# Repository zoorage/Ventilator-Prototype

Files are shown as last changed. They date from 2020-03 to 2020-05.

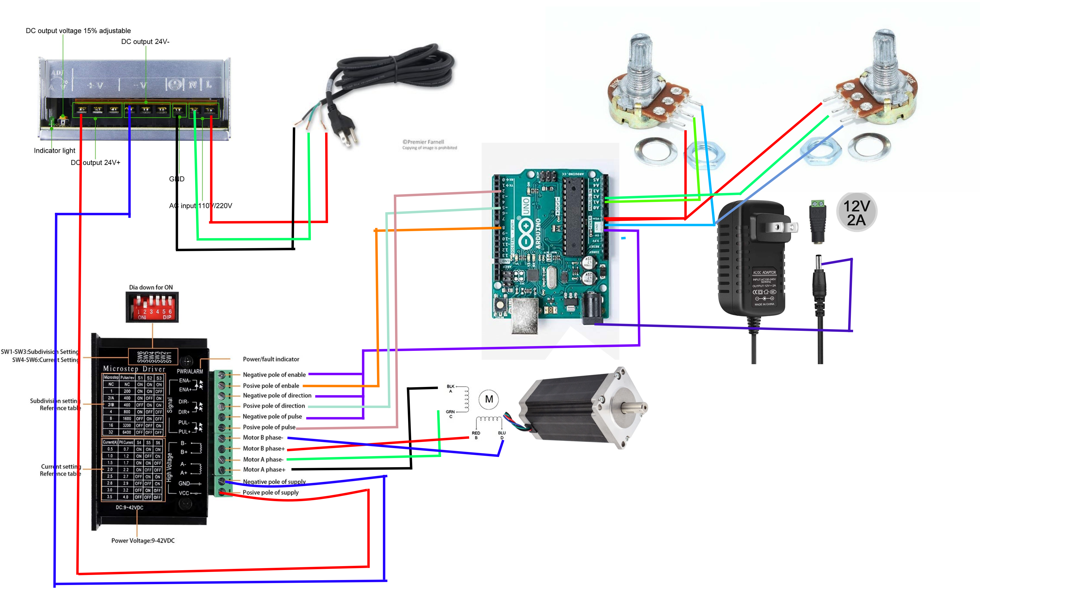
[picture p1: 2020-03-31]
Wiring Diagram.png

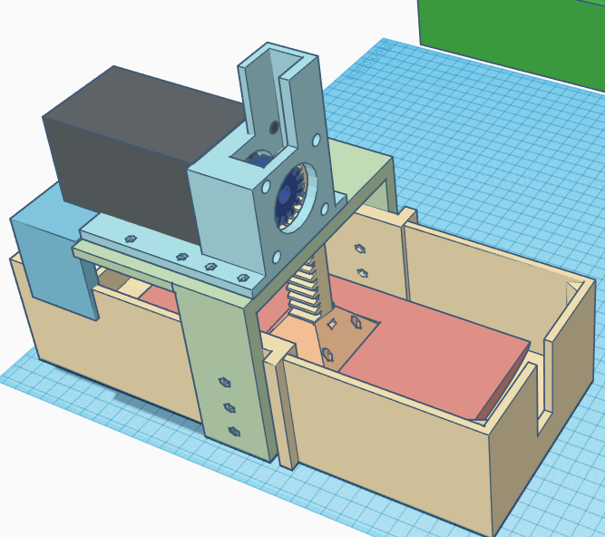
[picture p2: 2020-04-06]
3D Print Files/Vent Side 2.PNG

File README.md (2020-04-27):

# Ventilator-Prototype: Bridge to Mechanical Ventilation (Bridge)

Heads up, I have not been able to update the wiring diagram. The instructions has all the connections in it though.
Also, I will update the arduino sketch once I had the time to do a little more testing with the LED and reset/test button.

If anyone has experience with FDA applications for EUA and are able to help with this process, please contact me. I can use all the help I can get.

Disclaimers
1. This device is not approved by FDA or any other regulatory body.
2. This is not a ventilator or replacement for ventilators.
3. This device should never be used on a patient while there is an FDA approved device available.
4. Only practitioners who are fully competent in managing critically ill patients should consider this device.
5. There is absolutely no clinical testing done on this device. This device should be considered very high risk, and extreme caution should be exercised to consider using this device on a human being. In other workd, the only time the benefit of using this device may outweigh the risks would be when the patient is faced with certain death due to absence of any FDA approved devices or therapies.
6. Our team has provided this instruction as good samaritans for everyone and will not accept liability for any damages that the use of this device may cause.
7. Anyone who follows this instruction agrees to follow all the loal and federal regulatory protocols for compassionate use of investigational new devices and if applicable inform all the regulatory bodies such as FDA or local IRB.

This is an effort to create a make shift device to bridge patients infected with COVID-19 who need mechanical ventilation only when there is no ventilator available

I am an anesthesiologist with no real technical background.
Basically, this is a simple prototype that is easily reproducible and costs about $100. It can be made very quickly and does not require any technical expertise.
I started working on this last week, when I heard about the total number of ventilators in my state and the number that we think we're going to need. In the back of my mind, I kept telling myself that we can just use a bag and ventilate the patients with hand, but we are going to have a drastic shortage of man power too. So I decided to make a system that would replace hand ventilation and is cheap, easy and NEVER TO BE USED ON A PATIENT unless shortage of ventilators mean my patient with a reversible respiratory failure is going to die. That is the only time that I would use a system like this. 
Once I fix my 3D printer's bed, I will post the more elegant prototype. 
Here I'm using and arduino with DRV 8825 driver for a NEMA 17 stepper motor. 
I'm working on a few other prototypes too and once I can do more testing, I will post the STL files, arduino sketch and the part list.
Again, this is not a ventilator replacement; this is only to be used when patients have no other options and will simply die without a ventilator.

My team is working on the FDA's EUA application and I will provide updates as soon as I can.

Shield: [][cc-by]

This work is licensed under a [Creative Commons Attribution 4.0 International
License][cc-by].

[][cc-by]

[cc-by]: http://creativecommons.org/licenses/by/4.0/
[cc-by-image]: https://i.creativecommons.org/l/by/4.0/88x31.png
[cc-by-shield]: https://img.shields.io/badge/License-CC%20BY%204.0-lightgrey.svg

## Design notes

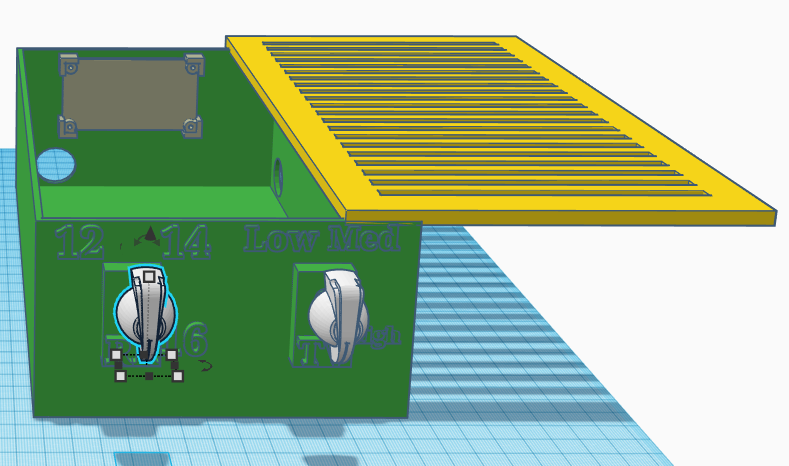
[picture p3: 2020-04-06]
3D Print Files/Vent-Electronics Box.PNG

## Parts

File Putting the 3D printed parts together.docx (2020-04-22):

Assembly of 3D-Printed Parts

1. Insert an M3 not in the circled slot on the gear and fasten an M3 bolt gently into it so that it won’t move.

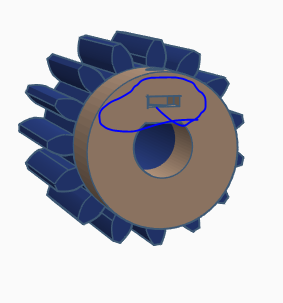
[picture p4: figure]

2. Insert the gear over the shaft of the motor. This has to be a tight fit. You may need to use a heat gun, blow drier, or a press.

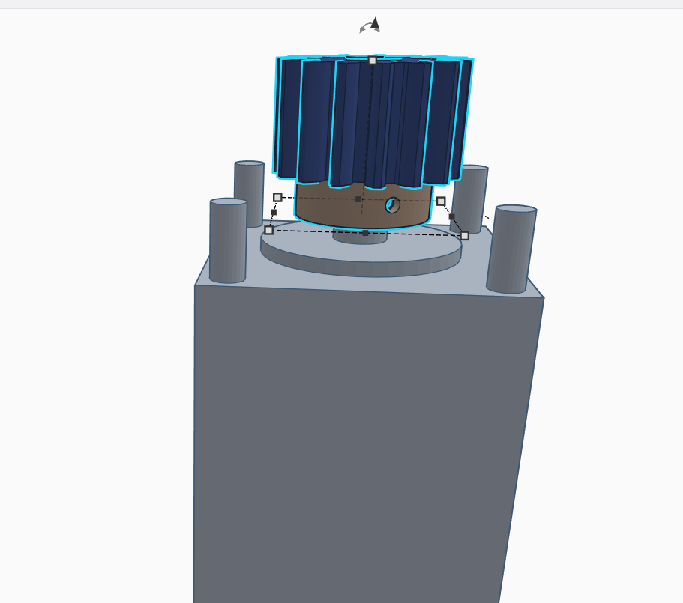
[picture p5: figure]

3. Use m4 nuts and bolts for the stepper motor and the motor cage.

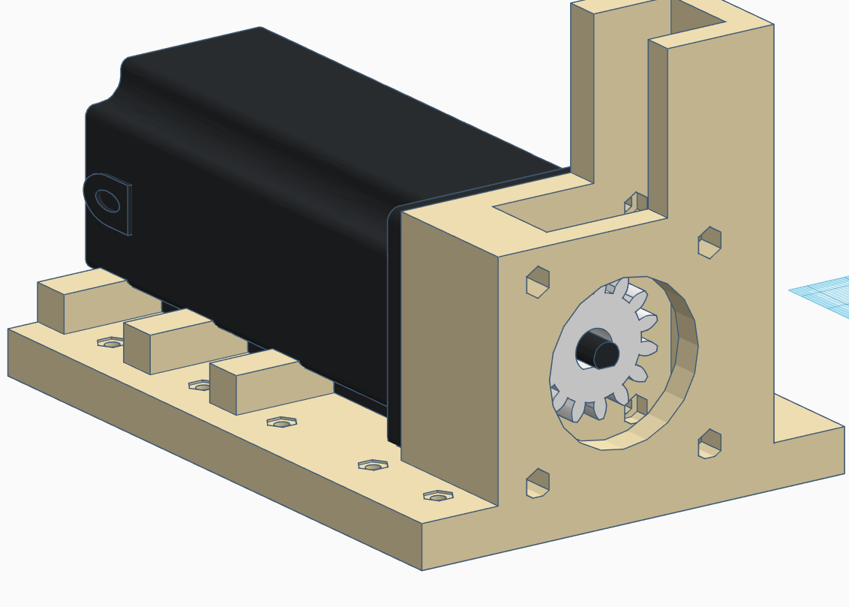
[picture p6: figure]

4. Use m2 nuts and bolts to secure the motor cage to the bridge.

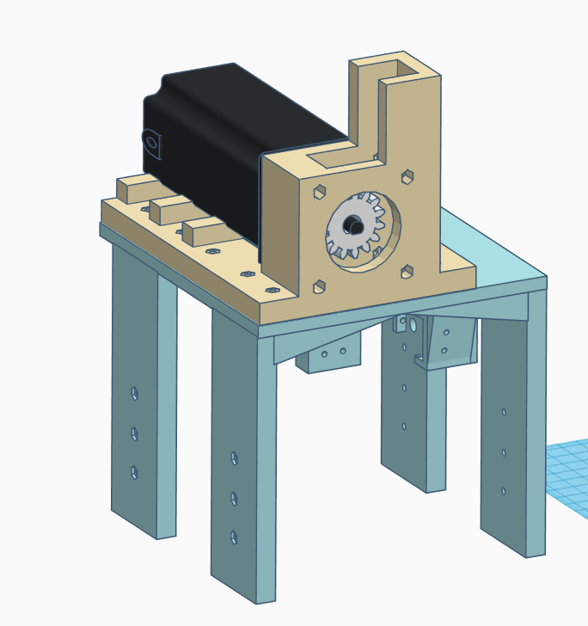
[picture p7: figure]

5. Insert an M3 nut in to the rack

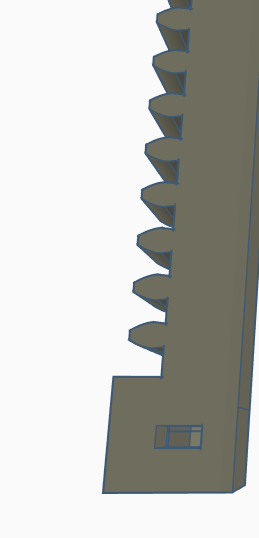
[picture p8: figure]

6. Place the rack into the rack base and insert an m3 bolt into the slot.

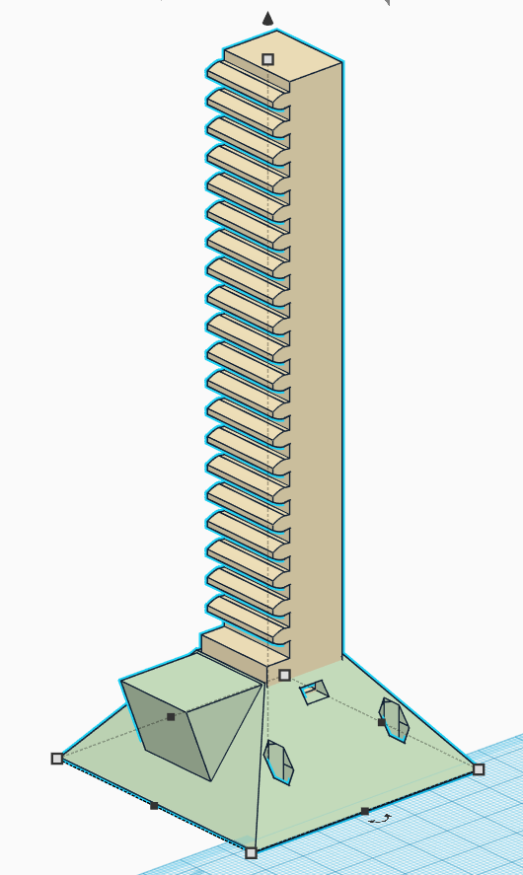
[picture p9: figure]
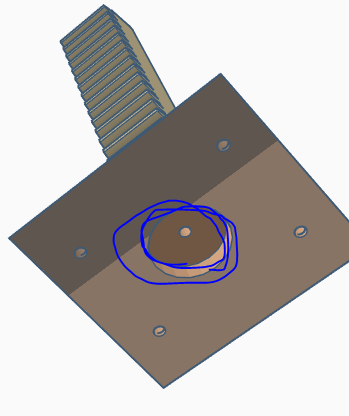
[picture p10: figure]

7. Use M3 nuts and bolts to secure the rack base to the plate.

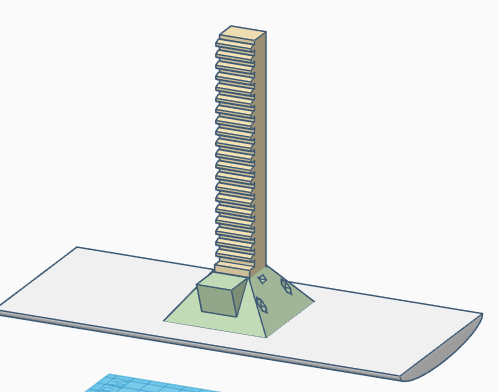
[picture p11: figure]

8. Insert the rack through the motor cage


9. Use M3 nuts and bolts to secure the bridge to the vent Box on the side facing the rack teeth.
  - Use M2 nuts and bolts to secure the two limit switches to the bottom of the bridge


10. Use M3 nuts and bolts to secure the bridge and vent Box to the electronics box on the side opposite to the rack teeth.


11. Insert the Lid over the electronics box.


12. Secure the Arduino (red), Arduino Sound Module (white) and the optional Arduino Buck (green) Converter on the specified Blocks.


13. Insert the above items as well as the Power Switch, RR and TV Adjustment Knobs, Stepper Motor Driver Universal Power Supply, and LED indicators in the electronics box.

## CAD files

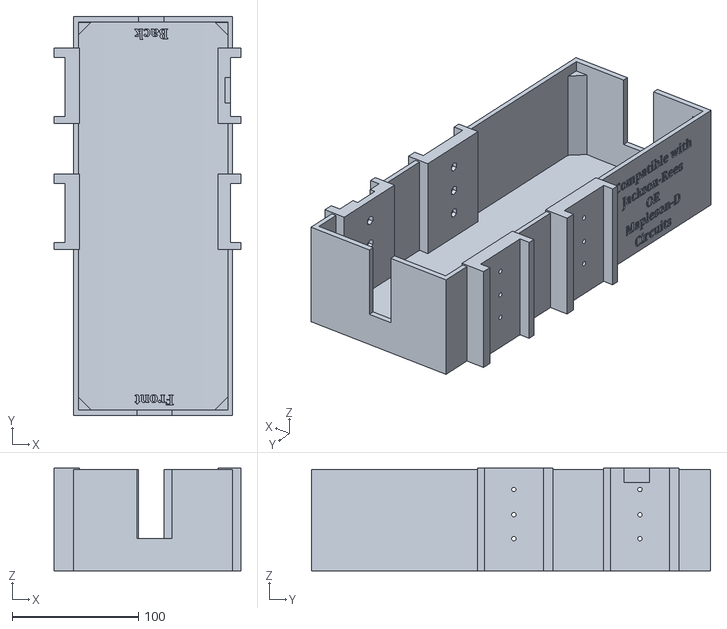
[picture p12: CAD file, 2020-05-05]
3D Print Files/V15/V15 VentBox.stl
148.0 x 316.5 x 81.4

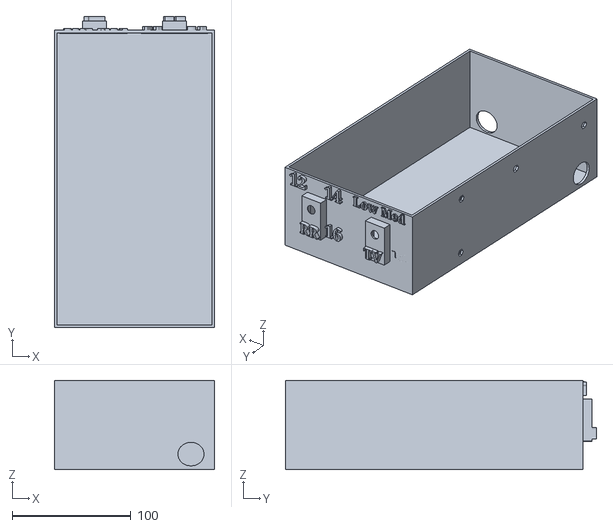
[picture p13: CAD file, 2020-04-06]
3D Print Files/V4 Electronix Box.stl
135.0 x 261.8 x 75.0

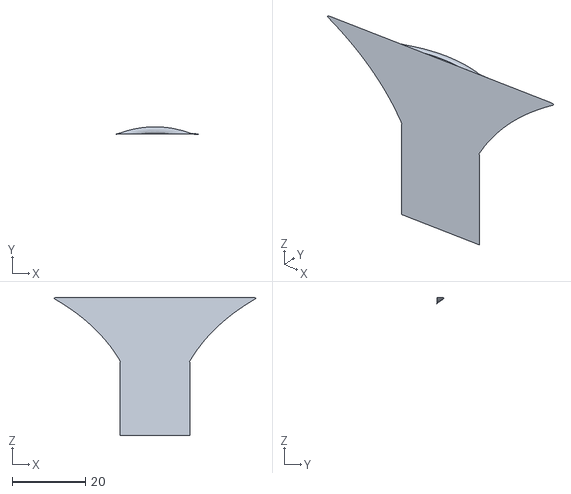
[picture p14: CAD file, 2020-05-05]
3D Print Files/V15/V15 SoundMod3of3.stl
55.0 x 1.99 x 37.6

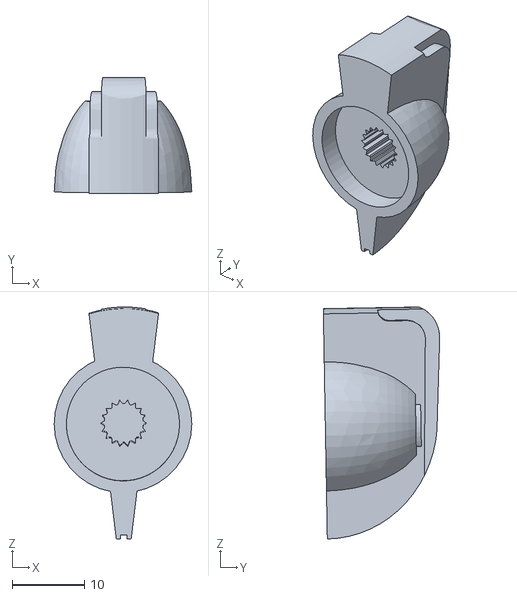
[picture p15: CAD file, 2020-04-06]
3D Print Files/V4 Potentio Knob.stl
19.0 x 16.1 x 32.0

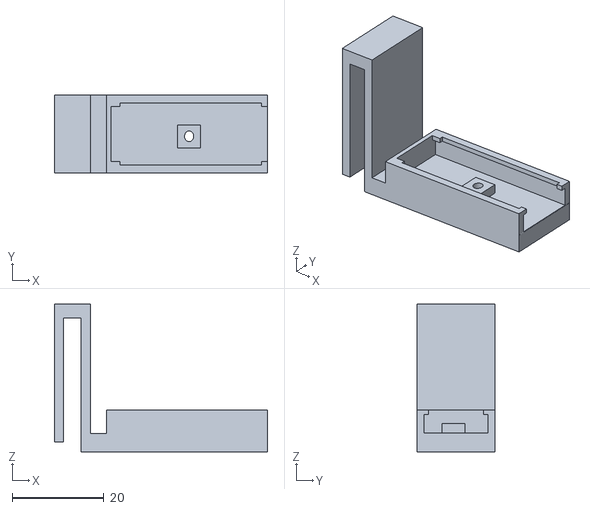
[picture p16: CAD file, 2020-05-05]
3D Print Files/V15/V15 SoundMod1of3.stl
46.3 x 17.0 x 32.1

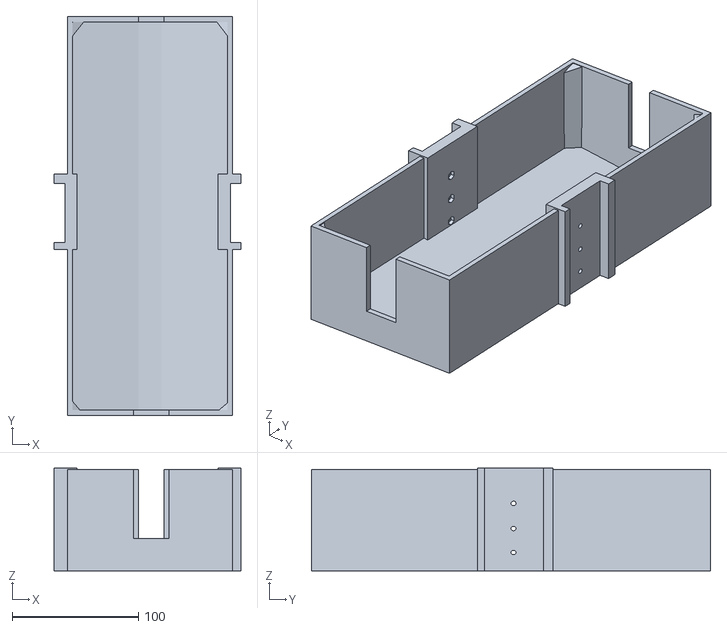
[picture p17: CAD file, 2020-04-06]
3D Print Files/V4 Vent Box.stl
148.0 x 316.5 x 81.4

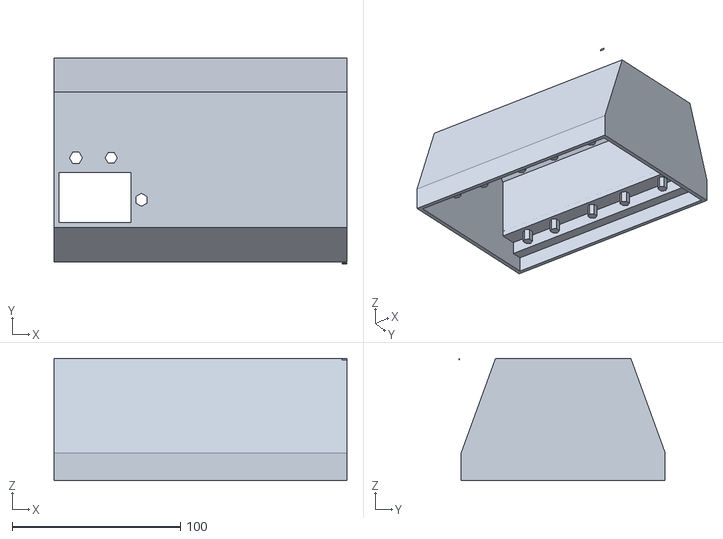
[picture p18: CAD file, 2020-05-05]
3D Print Files/V15/V15 ChimneyCover1of2.stl
174.4 x 122.5 x 72.9

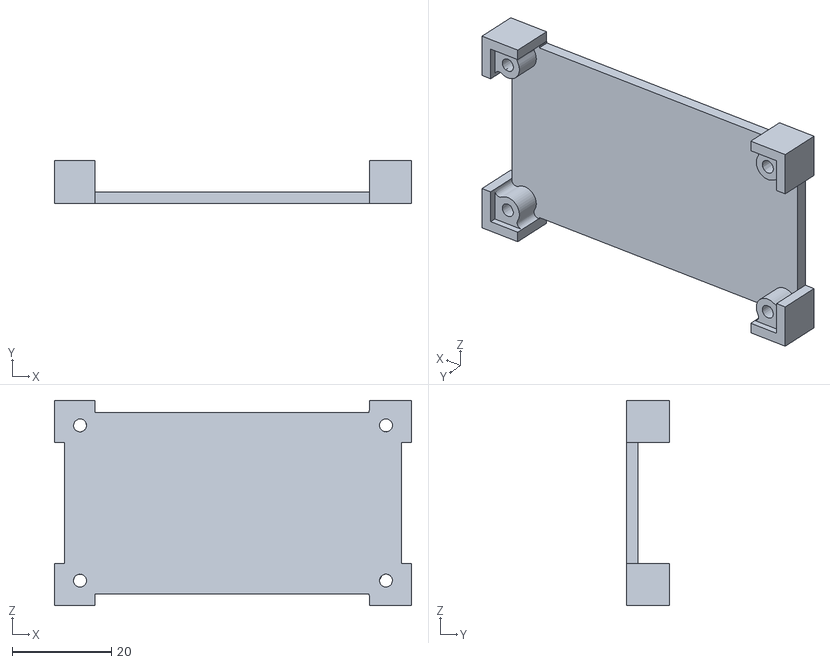
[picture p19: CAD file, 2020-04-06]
3D Print Files/V4 Buck Converter Case.stl
72.1 x 8.76 x 41.5

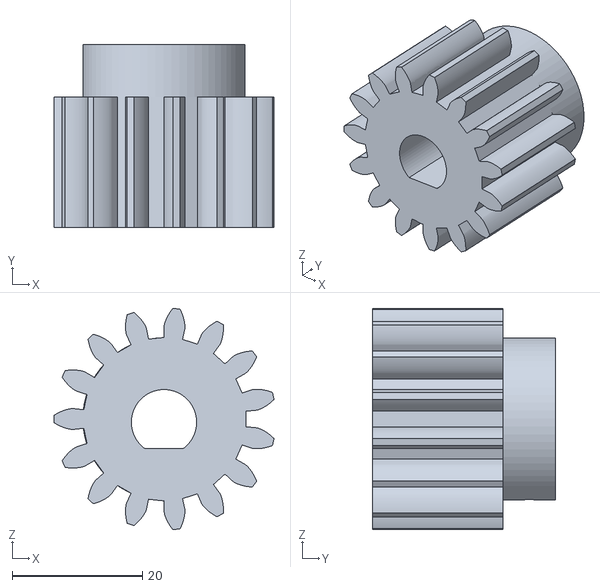
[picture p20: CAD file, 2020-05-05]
3D Print Files/V15/V15 Gear.stl
33.7 x 28.0 x 33.9

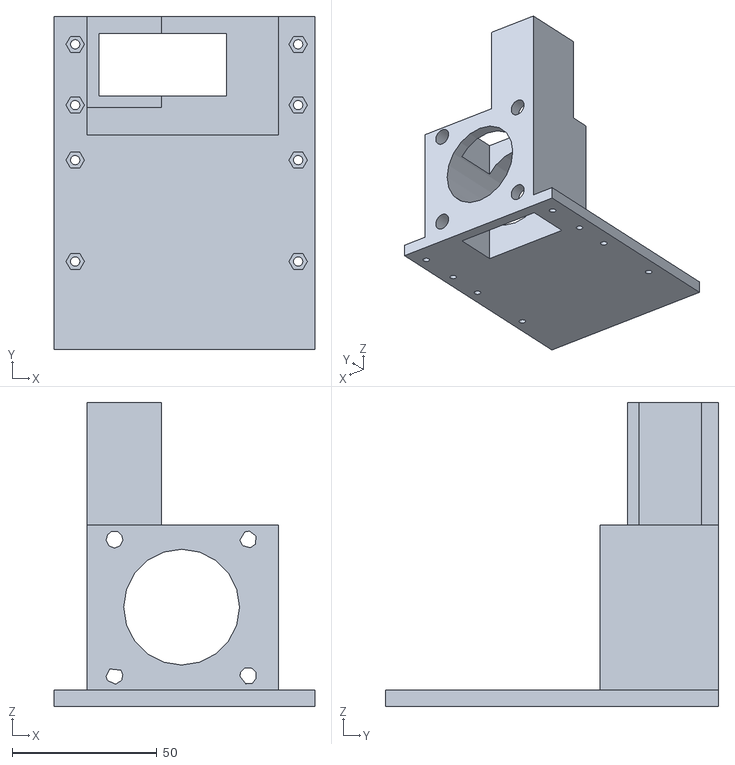
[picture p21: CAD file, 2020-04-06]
3D Print Files/V4 Vent Motor Cage.stl
90.0 x 115.0 x 105.0

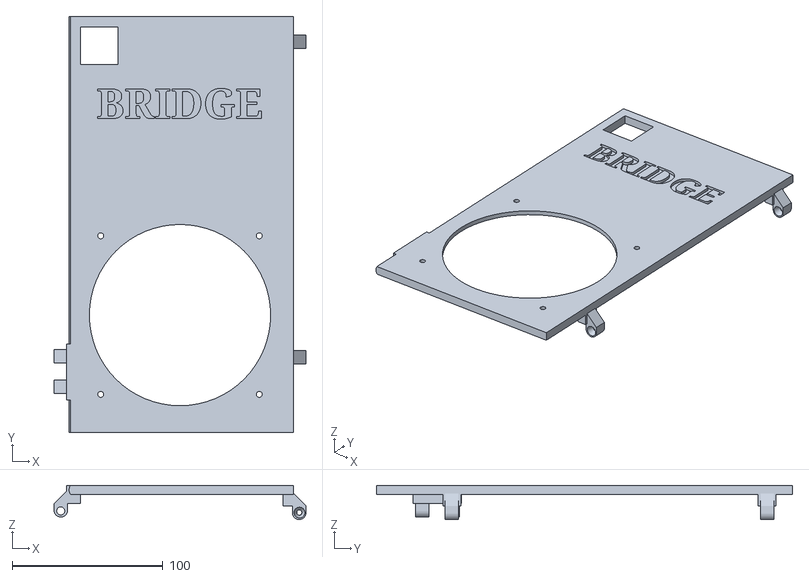
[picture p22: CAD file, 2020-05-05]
3D Print Files/V15/V15 Electronics Cover.stl
166.9 x 275.5 x 22.6

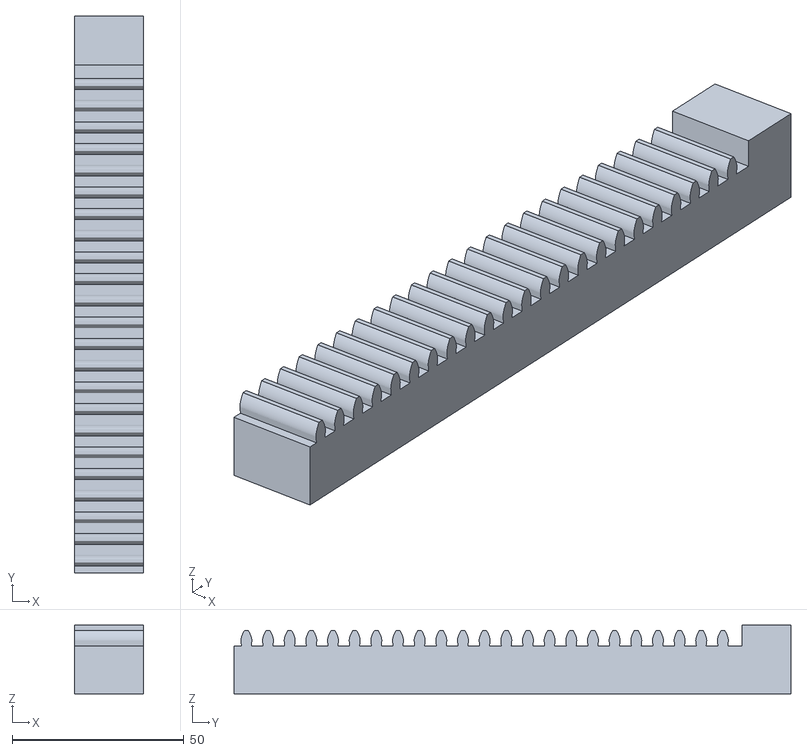
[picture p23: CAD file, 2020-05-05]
3D Print Files/V15/V15 Rack.stl
20.0 x 162.0 x 20.0

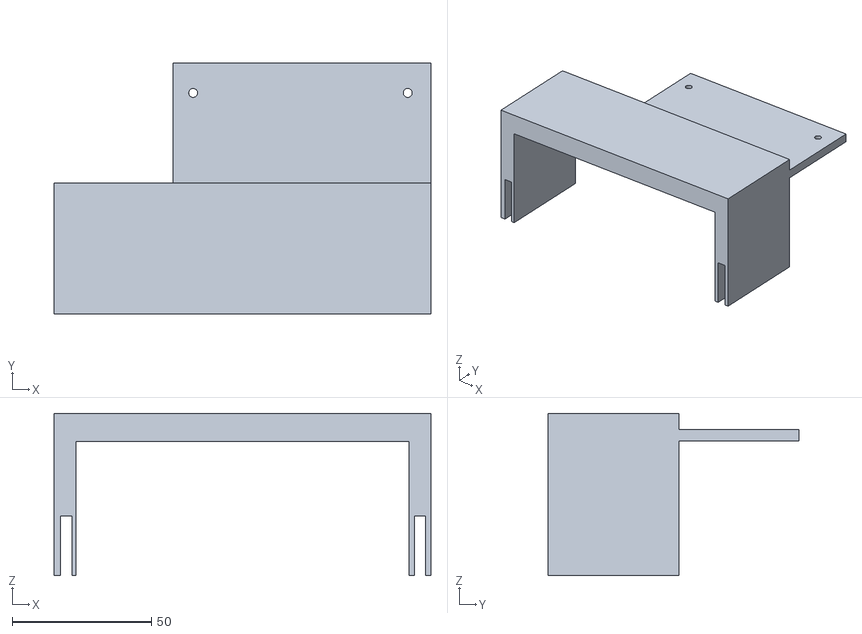
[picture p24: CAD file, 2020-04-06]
3D Print Files/V4 Vent Back Motor Base.stl
135.3 x 89.9 x 58.2

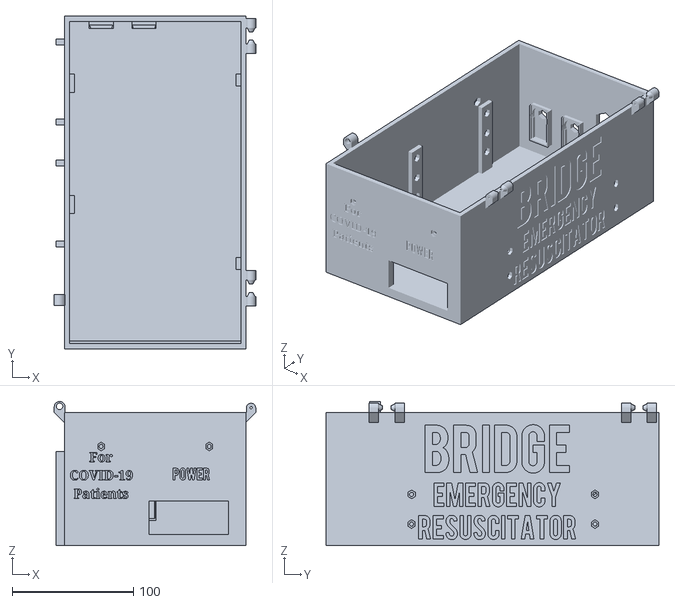
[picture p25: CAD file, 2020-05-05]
3D Print Files/V15/V15 Electronics Box.stl
166.5 x 275.0 x 119.1

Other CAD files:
3D Print Files/V4 Vent Gear.stl
3D Print Files/V4 Electronix Box Lid.stl
3D Print Files/V15/V15 RackBase.stl
3D Print Files/V4 Vent Plate.stl
3D Print Files/V13/V13 Arduino Case.stl
3D Print Files/V13/V13 Bridge.stl
3D Print Files/V13/V13 Buck Converter Case.stl
3D Print Files/V13/V13 Chimney Cover.stl
3D Print Files/V13/V13 ElectronicsBox.stl
3D Print Files/V13/V13 ElectronicsBoxLid.stl
3D Print Files/V13/V13 Gear.stl
3D Print Files/V13/V13 Knob.stl
3D Print Files/V13/V13 Motor Chimney.stl
3D Print Files/V13/V13 Plate.stl
3D Print Files/V13/V13 Rack.stl
3D Print Files/V13/V13 RackPlate.stl
3D Print Files/V13/V13 SoundAmp1of2.stl
3D Print Files/V13/V13 SoundAmp2of2.stl
3D Print Files/V13/V13 SoundModuleCase.stl
3D Print Files/V13/V13 VentBox.stl
3D Print Files/V15/V15 ArduinoBuckCase.stl
3D Print Files/V15/V15 Bridge.stl
3D Print Files/V15/V15 Chimney.stl
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

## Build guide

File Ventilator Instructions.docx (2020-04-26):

Contributors to this project:

-Borzoo Farhang, DO, MS, MSHS

Assistant Professor of Anesthesiology

University of Vermont Medical Center

borzoo.farhang@gmail.com

-Alec Gill

-Tom Caulton

1. Part List:
  a. NEMA 23 Stepper Motor: $39.99

https://www.amazon.com/gp/product/B00PNEPW4C/ref=ppx_yo_dt_b_asin_title_o04_s00?ie=UTF8&psc=1

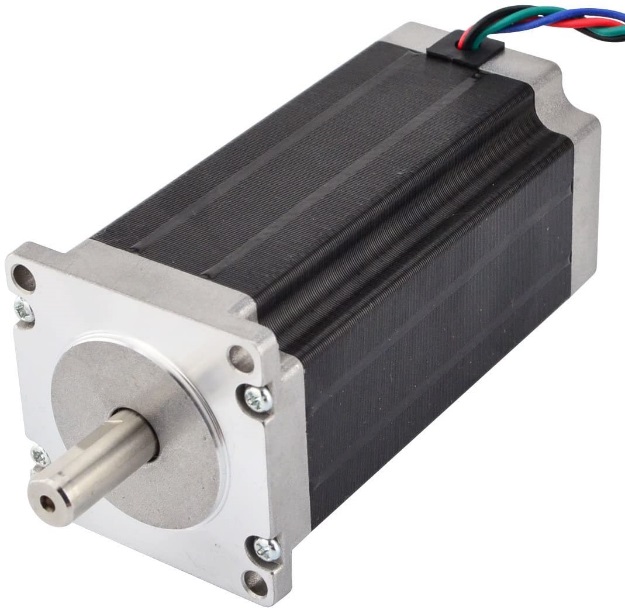
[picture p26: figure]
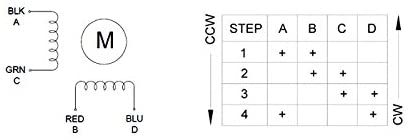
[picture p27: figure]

b.

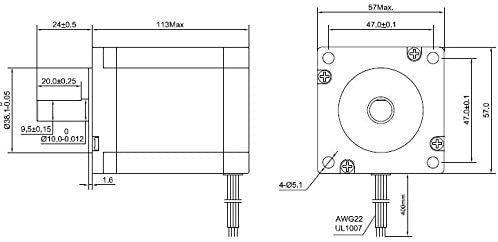
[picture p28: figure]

  b. TB6600 Stepper Motor Driver: $10.75

https://www.amazon.com/gp/product/B0839BBFVZ/ref=ppx_yo_dt_b_asin_title_o07_s00?ie=UTF8&psc=1

Or: 9.99

https://www.ebay.com/itm/Stepper-Motor-Driver-TB6600-4A-DC9-40V-for-Nema17-Nema23-Nema34-42-57-86mm/123554326786?ssPageName=STRK%3AMEBIDX%3AIT&_trksid=p2057872.m2749.l2648

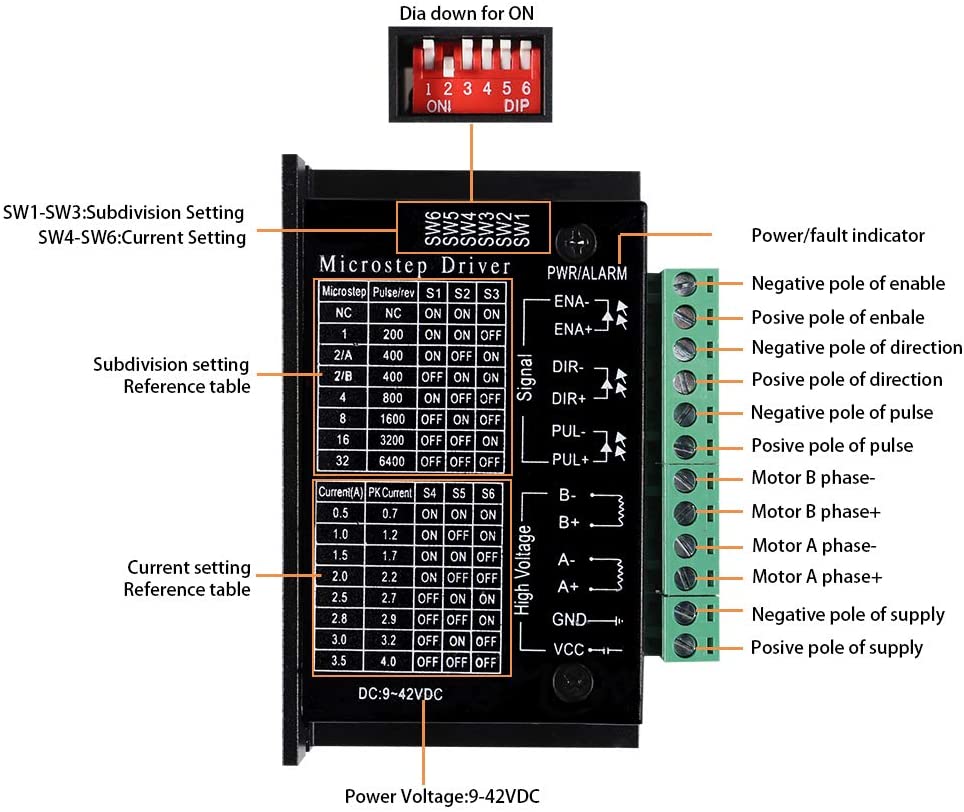
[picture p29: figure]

  c. ARDUINO UNO R3: $19.89

https://www.amazon.com/gp/product/B008GRTSV6/ref=ppx_yo_dt_b_asin_title_o04_s00?ie=UTF8&psc=1

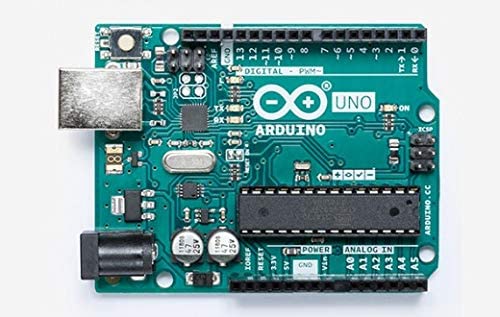
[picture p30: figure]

  d. Power Supply for Arduino:
    i. $8.69

https://www.amazon.com/gp/product/B01GD4ZQRS/ref=ppx_yo_dt_b_search_asin_title?ie=UTF8&psc=1

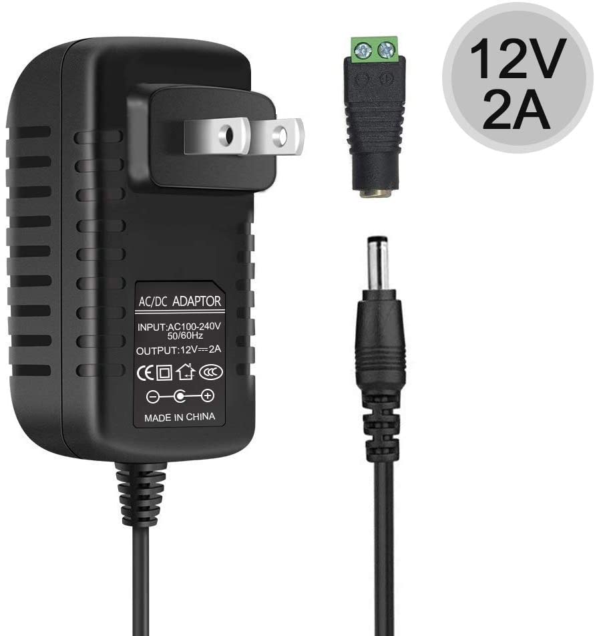
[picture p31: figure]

    ii. Alternatively: Buck converter $5.95

LM2596s Buck Converter DC to DC Step-down Voltage Regulator Power Module 36V 24V 12V to 5V 2A Voltage Stabilizer with LED Display

https://www.amazon.com/gp/product/B07CVBG8CT/ref=ppx_yo_dt_b_search_asin_title?ie=UTF8&psc=1

  e. Power Supply for the Motor: $24.99

https://www.amazon.com/gp/product/B06XK2ZNKC/ref=ppx_yo_dt_b_asin_title_o05_s00?ie=UTF8&psc=1

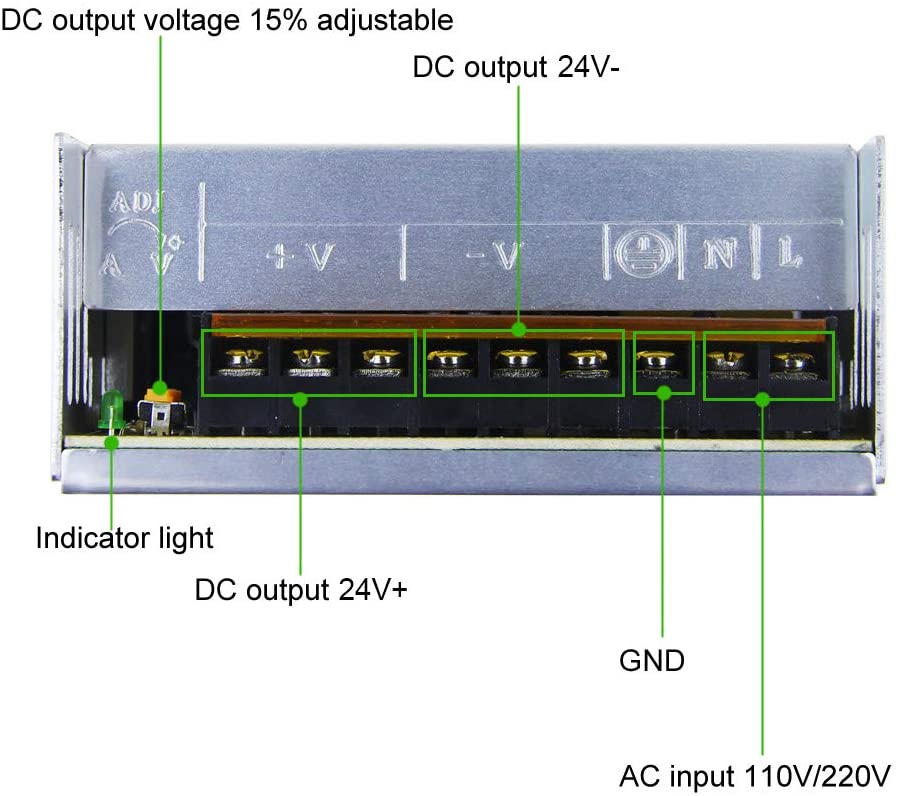
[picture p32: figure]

  f. LED Indicator Red-Green $15.53

https://www.digikey.com/product-detail/en/dialight/5571402203F/350-2756-ND/2430778

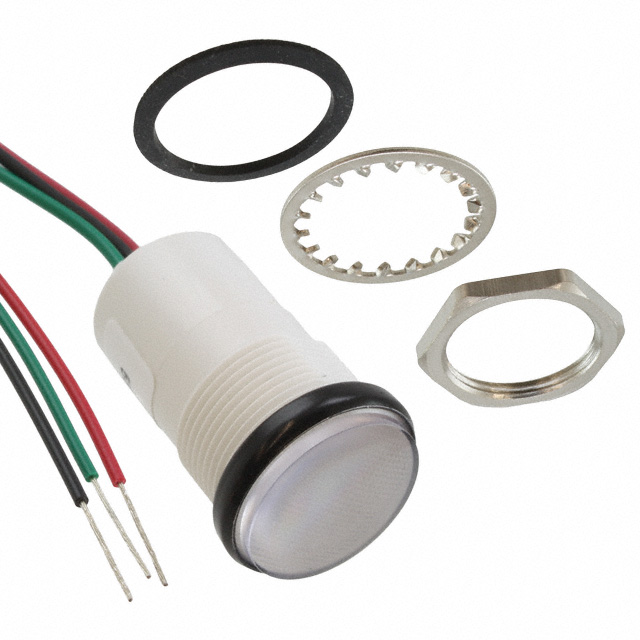
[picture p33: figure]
5571402203F Dialight | 350-2756-ND DigiKey Electronics

  g. Limit Switches $0.79 (URBEST AC 250V 5A SPDT 1NO 1NC Momentary Hinge Roller Lever Micro Switches 3 Pins 10 Pcs)

https://www.amazon.com/gp/product/B00MFRMFS6/ref=ppx_yo_dt_b_asin_title_o07_s00?ie=UTF8&psc=1

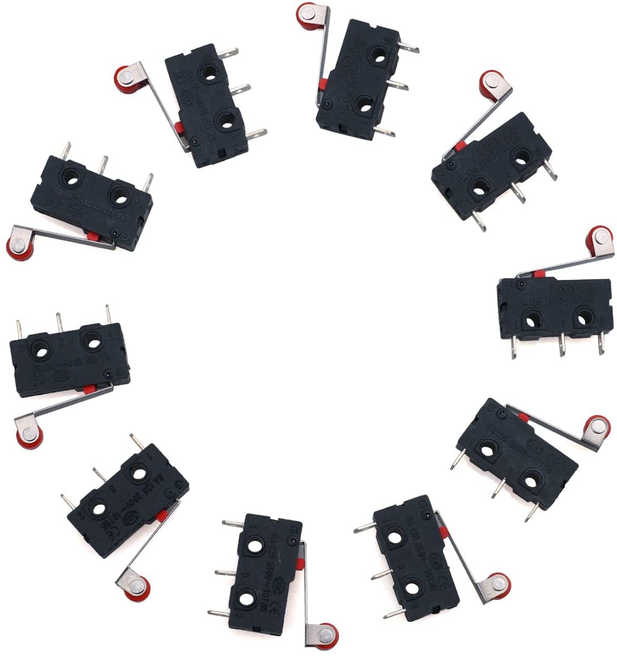
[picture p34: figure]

  h. Arduino Sound Module $1.56 (Oiyagai 5pcs DC 3.3-5V Passive Low Level Trigger Buzzer Alarm Sound Module for Arduino)

https://www.amazon.com/gp/product/B0777P6FN5/ref=ppx_yo_dt_b_asin_title_o06_s00?ie=UTF8&psc=1

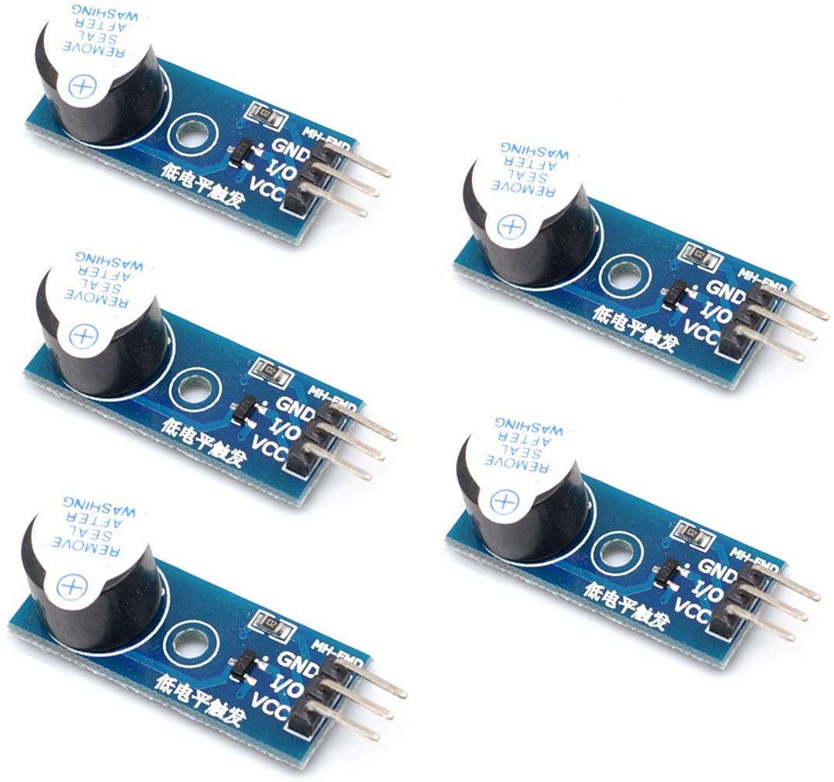
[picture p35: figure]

  i. Power Switch (still deciding)
  j. Push Button $10.50

https://www.digikey.com/product-detail/en/e-switch/PV0H240SS-341/EG5391-ND/5964418

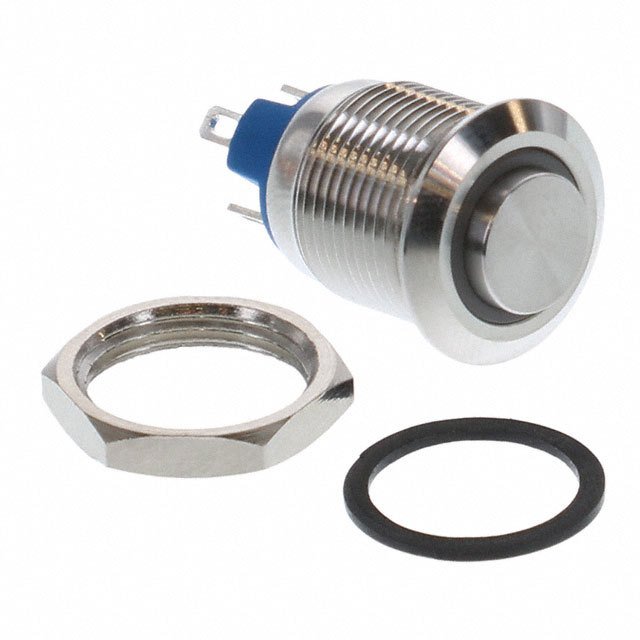
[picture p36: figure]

  k. Optional Power Connector $8.66 Qualtek 761-18/003

https://www.digikey.com/product-detail/en/qualtek/761-18-003/Q300-ND/417914

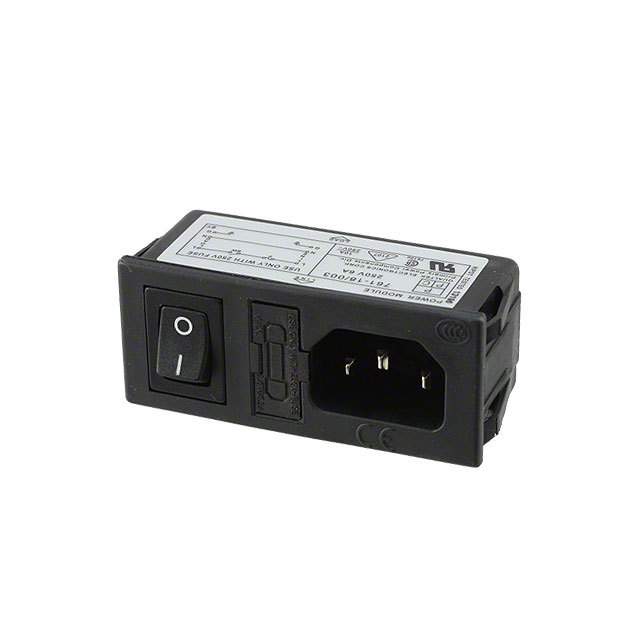
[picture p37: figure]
761-18/003 Qualtek | Q300-ND DigiKey Electronics

  l. Potentiometer (Optional): $0.5

https://www.ebay.com/itm/20pcs-10K-ohm-Linear-Taper-Rotary-Potentiometer-Panel-pot-B10K-15mm/392123626642?ssPageName=STRK%3AMEBIDX%3AIT&_trksid=p2057872.m2749.l2649

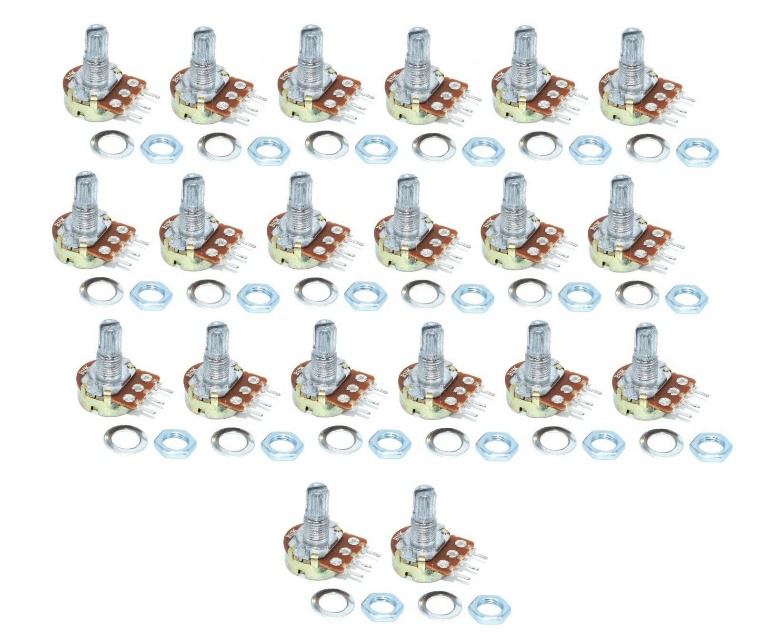
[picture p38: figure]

Optional Tools and Accessories:

a. Jumper Cables: $6.90

https://www.amazon.com/gp/product/B01EV70C78/ref=ppx_yo_dt_b_search_asin_title?ie=UTF8&psc=1

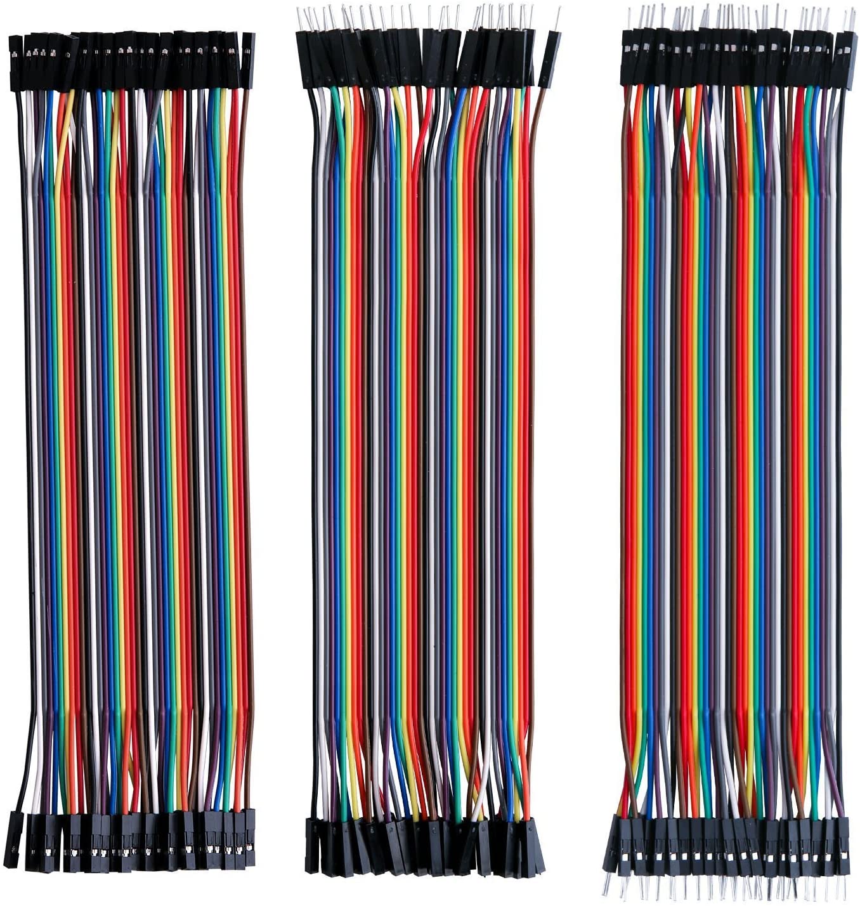
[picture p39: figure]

b. Screws: $24.99

https://www.amazon.com/gp/product/B07H4MG7TC/ref=ppx_yo_dt_b_asin_title_o04_s00?ie=UTF8&psc=1

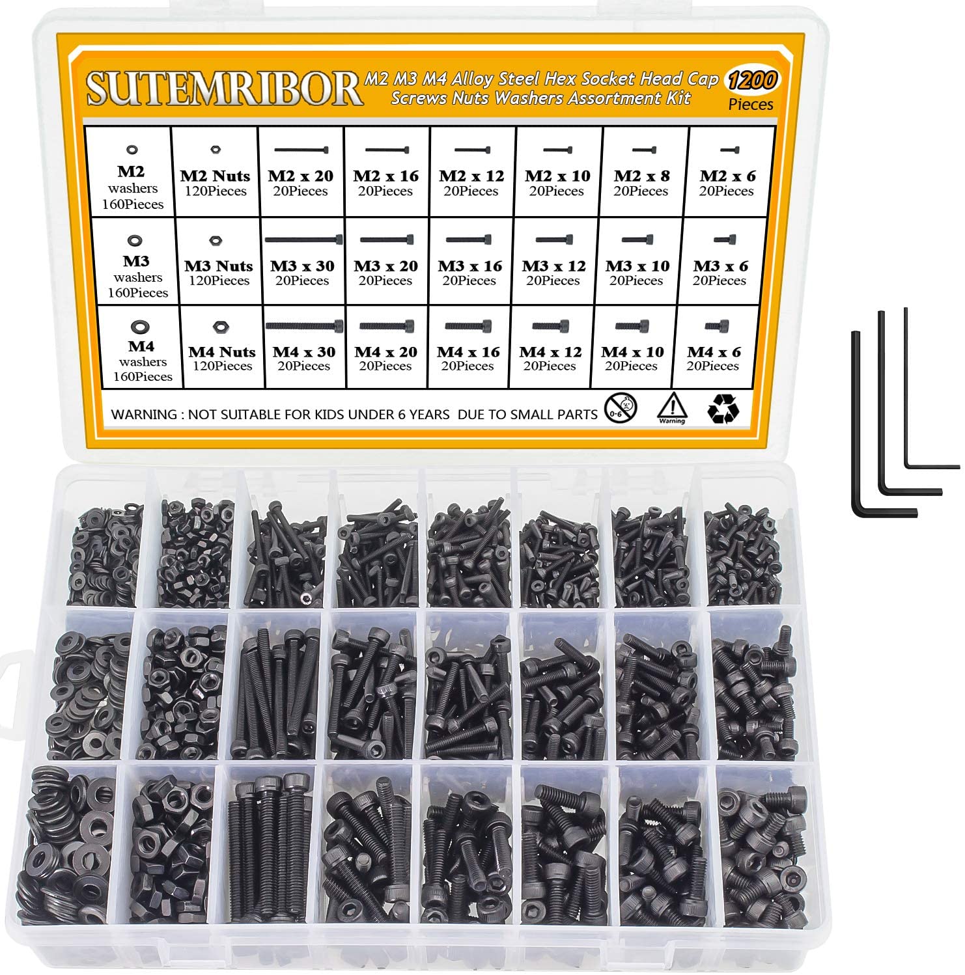
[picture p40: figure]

c. There are a few sets of wires to combine like the + of potentiometer 1 and 2. You can use any of the technics below:
    i. a crimping tool ($40.39) (https://www.amazon.com/gp/product/B002AVVO7K/ref=ppx_yo_dt_b_search_asin_title?ie=UTF8&psc=1) with Dupont connectors (27.99) (https://www.amazon.com/gp/product/B078RRPRQZ/ref=ppx_yo_dt_b_search_asin_title?ie=UTF8&psc=1)
    ii. Solder cables together and use electrical tape around it
    iii. Use a breadboard ($11.99) (https://www.amazon.com/gp/product/B0727X6N9D/ref=ppx_yo_dt_b_search_asin_title?ie=UTF8&psc=1)
    iv. Use PCB board ($12.99) https://www.amazon.com/gp/product/B079DN31SW/ref=ppx_yo_dt_b_search_asin_title?ie=UTF8&psc=1
d. Connections:

From Device | From | To | | To Device
15A Power Supply for Motor | L | L (Live) of Line to the wall | | 120V Outlet
| N | N (Neutral) of Line to the wall
| Ground | Ground of Line to the wall
| V- | GND on Stepper Driver | | TB 6600 Stepper Driver
| V+ | VCC on Stepper Driver
| V- (optional) | V- In on Buck Converter | | Buck Converter
| V+ (optional) | V+ In on Buck Converter
TB 6600 Stepper Driver | VCC | V+ | | 15A Power Supply for Motor
| GND | V-
| A+ | Black Wire | | Stepper Motor
| A- | Green Wire
| B+ | Red Wire
| B- | Blue Wire
| PUL+ | 9 | | Arduino
| PUL- | GND (Combine PUL-, DIR- and ENA- all and connect to GND of Arduino)
| DIR+ | 8
| DIR- | GND (Combine PUL-, DIR- and ENA- all and connect to GND of Arduino)
| ENA+ | 13
| ENA- | GND (Combine PUL-, DIR- and ENA- all and connect to GND of Arduino)
Stepper Motor | Black Wire | A+ | | TB 6600 Stepper Driver
| Green Wire | A-
| Red Wire | B+
| Blue Wire | B-
Arduino | 8 | DIR+ | | TB 6600 Stepper Driver
| 9 | PUL+
| 13 | ENA+
| A0 | Middle Pin Potentiometer 1 (Tidal Volume) | | Potentiometer 1 and 2
| A1 | Middle Pin Potentiometer 2 (Resp. Rate)
| 5V | + (Combine + of potentiometer 1 and 2 and connect to Vin)
| GND | - (Combine - of potentiometer 1 and 2 and connect to GND)
| GND | Combine PUL-, DIR- and ENA- all and connect to GND of Arduino | | TB 6600 Stepper Driver
| Power Supply Connection (or Buck Converter below) | 12V Power Adaptor
| Vin | V+ Out | Buck Converter (Or Power Supply above)
| GND | V- Out
| 6 | + | Arduino Sound Module
| GND | -
| 3 | NC | Top Limit Switch
| | Common
| 2 | NC | Resp. Verify Limit Switch
| | Common
Potentiometer 1 and 2 | Middle Pin Potentiometer 1 | A0 | Arduino
| Middle Pin Potentiometer 2 | A1
| + (Combine + of potentiometer 1 and 2 and connect to Vin) | 5V
| - (Combine - of potentiometer 1 and 2 and connect to GND) | GND
Arduino Sound Module | + | 6 | Arduino
| - | GND
Top Limit Switch | NC | 3
| Common | GND
Resp. Rate Verify Limit Switch | NC | 2
| Common | GND
LED Light | + | 5V
| Green | TBD
| Red | TBD
Reset Switch | + | TBD
| - | GND

e. Settings:
  a. TB 6600 Driver:

Set on the side controller of the driver

1 | Off (Up)
2 | Off (Up)
3 | Off (Up)
4 | Off (Up)
5 | Off (Up)
6 | Off (Up)

  b. Arduino:

Code can be found at:

https://github.com/zoorage/Ventilator-Prototype.git

f. Video of Earlier Prototypes:

https://www.youtube.com/watch?v=NUu_Q0IXxf4

https://www.youtube.com/watch?v=SI2yv-K0nfQ

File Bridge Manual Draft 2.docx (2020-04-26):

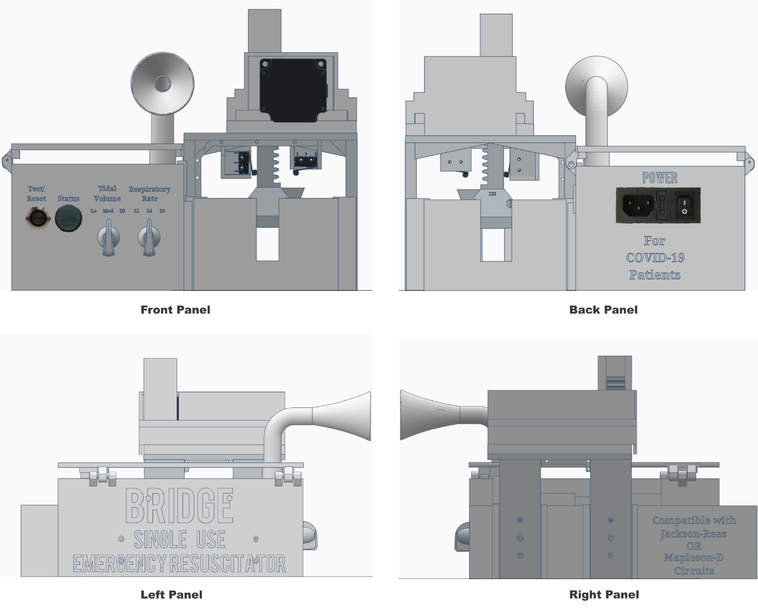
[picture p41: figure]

Contact Information

Borzoo Farhang, DO, MS, MSHS

Assistant Professor of Anesthesiology and Perioperative Medicine

University of Vermont Medical Center

Larner College of Medicine

111, Colchester Ave

Burlington, VT 05401

(802) 881-9927

borzoo.farhang@uvmhealth.org

Warranty and Liability

The Bridge Ventilator is not approved by FDA or any other regulatory body for routine use in clinical care. This device has been designed as a rescue therapy (bridge to mechanical ventilation) during the COVID-19 pandemic for patients who require mechanical ventilation while there are no FDA approved ventilators available. This device is not a replacement for an FDA approved ventilator and should never be used on a patient while there is an FDA approved device available. Only practitioners who are fully competent in managing critically ill patients should consider this device.

This device has not undergone any clinical testing. This device should be considered very high risk, and extreme caution should be exercised in considering using this device on a patient. In other word, the only time that the benefits of using this device may outweigh the risks would be when the patient is faced with certain death due to absence of any FDA approved devices or therapies.

The design and instructions of the Bridge ventilator is released as an open source project. Our team has provided this instruction to public to aid others in their effort in creating their own designs and improve upon ours. We will not accept liability for any damages that the use of this device may cause.

Anyone who follows uses this device agrees to refrain from deviations from the instructions provided in this manual and also agrees to follow all the local and federal regulatory protocols for compassionate use of investigational new devices and inform all the regulatory bodies such as FDA, IRB, etc.

The Bridge ventilator is designed as a single-patient-use device. It should not be used on multiple patients.

This device does not contain any warranty.

We do not accept any liability should the use of this device result in harm, and operators need to assess risk-benefit for individual patients.

Notice to Operators

Unsafe Operation - Operating the Bridge ventilator without a complete and thorough understanding of its attributes is unsafe and may cause harm to the patient. It is important that this manual be read and understood in its entirety before operating the ventilator.

The Bridge ventilator must be operated in conjunction with continuous end tidal CO2 monitoring. Failure to do so is unsafe and prohibited.

The Bridge ventilator is not equipped with a battery power, and in the case of loss of external power, there is no warning system with this device. Any patient connected to the Bridge ventilator must be continuously monitored by qualified healthcare providers with full monitoring of physiologic data in critical care setting.

The bridge ventilator requires either an adult Jackson-Rees or Mapleson D circuit to function. The specific circuits do not accompany the Bridge ventilator and have to be obtained by the ordering physician separately.

Warnings and Cautions Section - Read the section on Warnings and Cautions carefully before

operating the Bridge ventilator.

Use and Maintenance - Any questions regarding installing, operating, or maintaining the Bridge

ventilator should be directed to Borzoo Farhang.

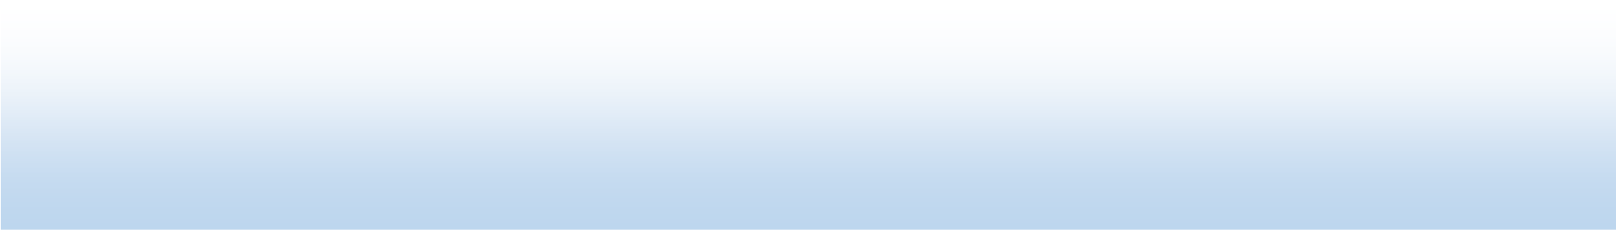
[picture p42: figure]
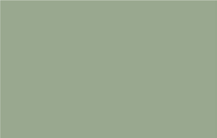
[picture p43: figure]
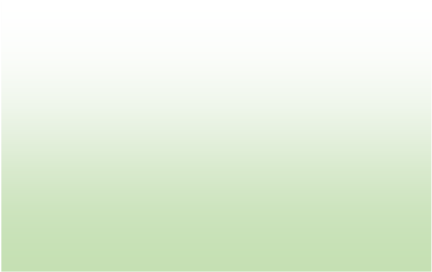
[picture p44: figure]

FACT SHEET FOR HEALTHCARE PROVIDERS Coronavirus

Emergency Use of Ventilators During the COVID-19 Pandemic March 24, 2020 Disease 2019

# (COVID-19)

This Fact Sheet informs you of the significant known and potential risks and benefits of the emergency use of ventilators, anesthesia gas machines modified for use as ventilators, and positive pressure breathing devices modified for use as ventilators (collectively referred to as “ventilators” in this Fact Sheet), ventilator tubing connectors, and ventilator accessories.

Certain ventilators, ventilator tubing connectors, and ventilator accessories are authorized for emergency use in healthcare settings for treatment of patients during the COVID-19 pandemic by their healthcare provider.

All patients who are treated with authorized ventilators during the COVID-19 pandemic will receive the Fact Sheet for Patients: Emergency Use of Ventilators During the

COVID-19 Pandemic

What are the symptoms of COVID-19?

Many patients with confirmed COVID-19 have developed fever and/or symptoms of acute respiratory illness (e.g., cough, difficulty breathing). However, limited information is currently available to characterize the full spectrum of clinical illness associated with COVID-19. Based on what is known about the virus that causes COVID-19, signs and symptoms may appear any time from 2 to 14 days after exposure to the virus. Based on preliminary data, the median incubation period is approximately 5 days, but may range 2-14 days.

Public health officials have identified cases of COVID-19 infection throughout the world, including the United States, which may pose risks for public health. Please check the CDC webpage for the most up to date information.

What do I need to know about the emergency use of ventilators?

- Certain ventilators, ventilator tubing connectors, and ventilator accessories that meet certain criteria for safety, performance, and labeling have been authorized for emergency use.
- Ventilators found in the list of authorized products are authorized for use in healthcare settings for treatment of patients during the COVID-19 pandemic by their healthcare provider.
- For each device, healthcare providers should review the instructions for use, including device specifications, reprocessing instructions (if applicable), and other labeling information.
- During the COVID-19 pandemic, certain authorized ventilators may be used to support multiple patients using a continuous ventilator splitter. Healthcare providers should review additional device specifications, labeling, and patient monitoring recommendations in these circumstances.

Use appropriate personal protective equipment when caring for individuals suspected of having COVID-19 as outlined in the CDC Interim Infection Prevention and Control Recommendations for Patients with Confirmed

Coronavirus Disease 2019 (COVID-19) or Persons Under Investigation for COVID-19 in Healthcare Settings or on the CDC webpage on Infection Control.

Current information on COVID-19 for healthcare providers is available at CDC’s webpage, Information for Healthcare Professionals (see links provided in “Where can I go for updates and more information” section).

What are the known and potential benefits and risks of ventilators?

Potential benefits of ventilators include:

- Improved oxygenation and ventilation in the treatment of acute respiratory illness or difficulty breathing
- Life-supporting and potentially life-saving treatment

Potential risks of ventilators include:

- Device malfunctions or adverse events
- Potential infectious and mechanical complications from sharing one ventilator through the use of multiplexing adapters have not been studied, and therefore caution is advised
- Risks of modified ventilator devices have not been studied, and therefore caution is advised
- Risks associated with the potential reduced requirements for alarms and monitoring of patients
- Reduced familiarity of healthcare providers with novel technologies used to treat patients

What are the alternatives to traditional ventilators, and the known and potential benefits and risks of such products?

Alternatives to traditional ventilators that are authorized under this Emergency Use Authorization (EUA) include anesthesia gas machines modified for use as ventilators, and positive pressure breathing devices modified for use as ventilators.

Potential benefits of using alternatives to traditional ventilators include:

- Improved oxygenation and ventilation in the treatment of acute respiratory illness or difficulty breathing
- Life-supporting and potentially life-saving treatment

Potential risks of using alternatives to traditional ventilators include:

- A positive pressure breathing device cannot offer all of the support that a traditional mechanical ventilator can
- A positive pressure breathing device may expose others to aerosols that could be contagious
- Healthcare providers other than trained anesthesia providers may not be familiar with the operation of anesthesia equipment, and therefore should pay careful attention to the instructions for use to avoid use error

What is an EUA?

The United States FDA has made certain ventilators, anesthesia gas machines modified for use as ventilators, and positive pressure breathing devices modified for use as ventilators (collectively referred to as “ventilators”), ventilator tubing connectors, and ventilator accessories available under an emergency access mechanism called an Emergency Use Authorization (EUA). The EUA is supported by the Secretary of Health and Human Service’s (HHS’s) declaration that circumstances exist to justify the emergency use of medical devices, including alternative devices used as medical devices, due to shortages during the COVID-19 pandemic.

Ventilators, ventilator tubing connectors, and ventilator accessories made available under an EUA have not undergone the same type of review as an FDA-approved or cleared device. FDA may issue an EUA when certain criteria are met, which includes that there are no adequate, approved, available alternatives, and based on the totality of scientific evidence available, it is reasonable to believe that ventilators, ventilator tubing connectors, and ventilator accessories that meet certain criteria for safety, performance, and labeling may be effective in treatment of patients during the COVID-19 pandemic.

The EUA for ventilators, ventilator tubing connectors, and ventilator accessories is in effect for the duration of the COVID-19 declaration justifying emergency use of these devices, unless terminated or revoked (after which the products may no longer be used).

Where can I go for updates and more information?

CDC webpages:

General: (https://www.cdc.gov/nCoV)https://www.cdc.gov/COVID19 (https://www.cdc.gov/nCoV) (https://www.cdc.gov/nCoV)Healthcare Professionals:

https://www.cdc.gov/coronavirus/2019-nCoV/guidancehcp.html (https://www.cdc.gov/coronavirus/2019-nCoV/guidance-hcp.html) (https://www.cdc.gov/coronavirus/2019-nCoV/guidance-hcp.html)

Infection Prevention and Control Recommendations in Healthcare Settings:

https://www.cdc.gov/coronavirus/2019-ncov/infectioncontrol/control-recommendations.html (https://www.cdc.gov/coronavirus/2019-ncov/infection-control/control-recommendations.html) (https://www.cdc.gov/coronavirus/2019-ncov/infection-control/control-recommendations.html)

Infection Control: https://www.cdc.gov/coronavirus/2019 (https://www.cdc.gov/coronavirus/2019-ncov/infection-control/index.html)ncov/infection-control/index.html (https://www.cdc.gov/coronavirus/2019-ncov/infection-control/index.html) (https://www.cdc.gov/coronavirus/2019-ncov/infection-control/index.html)

FDA webpages:

General: www.fda.gov/novelcoronavirus (http://www.fda.gov/novelcoronavirus) EUAs: (includes links to patient fact sheet and manufacturer’s instructions) https://www.fda.gov/medical (https://www.fda.gov/medical-devices/emergency-situations-medical-devices/emergency-use-authorizations)devices/emergency-situations-medical-devices/emergency (https://www.fda.gov/medical-devices/emergency-situations-medical-devices/emergency-use-authorizations)use-authorizations (https://www.fda.gov/medical-devices/emergency-situations-medical-devices/emergency-use-authorizations) (https://www.fda.gov/medical-devices/emergency-situations-medical-devices/emergency-use-authorizations)

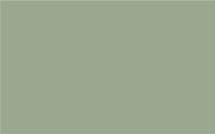
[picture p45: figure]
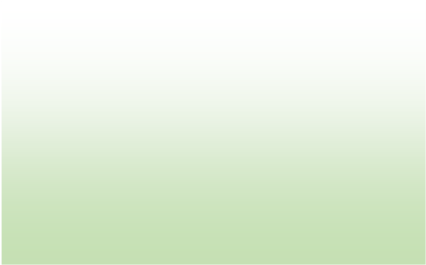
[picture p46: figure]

FACT SHEET FOR PATIENTS Coronavirus

Disease 2019

Emergency Use of Ventilators During the COVID-19 Pandemic March 24, 2020 (COVID-19)

You are being given this Fact Sheet because your healthcare provider believes it is necessary to provide you treatment using a ventilator, anesthesia gas machine modified for use as a ventilator, or positive pressure breathing device modified for use as a ventilator (collectively referred to as “ventilators” in this Fact Sheet), ventilator tubing connectors, and/or ventilator accessory.

This Fact Sheet contains information to help you understand the benefits and risks of using ventilators, ventilator tubing connectors, and ventilator accessories for the treatment of patients during the COVID-19 pandemic. After reading this Fact Sheet, if you have questions or would like to discuss the information provided, please talk to your healthcare provider.

- For the most up to date information on COVID-19 please visit the CDC Coronavirus Disease 2019 (COVID-19) webpage:
- https://www.cdc.gov/COVID19 (https://www.cdc.gov/nCoV) (https://www.cdc.gov/nCoV)

What is COVID-19?

COVID-19 is caused by the SARS-CoV-2 virus. The virus, which can cause mild to severe respiratory illness, was first identified in Wuhan, China, and has now spread globally, including the United States. There is limited information available to characterize the spectrum of clinical illness associated with COVID-19, but it likely spreads to others when a person shows signs or symptoms of being sick (e.g., fever, coughing, difficulty breathing, etc.).

What do I need to know about the emergency use of ventilators?

Certain ventilators, ventilator tubing connectors, and ventilator accessories that meet certain criteria for safety, performance, and labeling have been authorized under an Emergency Use Authorization (EUA) for emergency use in healthcare settings for treatment of patients during the COVID-19 pandemic by their healthcare provider.

A healthcare provider may choose to treat you with a ventilator if you have difficulty breathing, or other respiratory symptoms. During the COVID-19 pandemic, certain authorized ventilators may be used to support multiple patients using a continuous ventilator splitter when individual ventilators are not available, or preemptively to increase the potential of single-use ventilators for multiple patients simultaneously.

What is an EUA?

The United States FDA has made certain ventilators, anesthesia gas machines modified for use as ventilators, and positive pressure breathing devices modified for use as ventilators (collectively referred to as “ventilators”), ventilator tubing connectors, and ventilator accessories available under an emergency access mechanism called an EUA. The EUA is supported by the Secretary of Health and Human Service’s (HHS’s) declaration that circumstances exist to justify the emergency use of medical devices during the COVID-19 pandemic.

Ventilators, ventilator tubing connectors, and ventilator accessories made available under an EUA have not undergone the same type of review as an FDA-approved

• Where can I go for updates and more information? The most up-to-date information on COVID-19 is available at the CDC General webpage: https://www.cdc.gov/COVID19. (https://www.cdc.gov/nCoV) In addition, please also contact your healthcare provider with any questions/concerns.

1

FACT SHEET FOR PATIENTS Coronavirus

Disease 2019

Emergency Use of Ventilators During the COVID-19 Pandemic March 24, 2020 (COVID-19)

or cleared device. FDA may issue an EUA when certain criteria are met, which includes that there are no adequate, approved, available alternatives, and based on the totality of scientific evidence available, it is reasonable to believe that ventilators, ventilator tubing connectors, and ventilator accessories that meet certain criteria for safety, performance, and labeling may be effective in treatment of patients during the COVID-19 pandemic.

The EUA for ventilators, ventilator tubing connectors, and ventilator accessories is in effect for the duration of the COVID-19 declaration justifying emergency use of these devices, unless terminated or revoked (after which the products may no longer be used).

What are the known and potential benefits and risks of ventilators?

Potential benefits of ventilators include:

- Ventilator support may be effective in treating you if you have difficulty breathing, or other respiratory symptoms
- The use of a ventilator may help your condition improve and allow you to recover
- Life-supporting and potentially life-saving treatment

Potential risks of ventilators include:

- Modified ventilator devices and techniques may have new risks associated with them that have not been studied

What are the alternatives to traditional ventilators, and the known and potential benefits and risks of such products?

Alternatives to traditional ventilators that are authorized under this EUA include anesthesia gas machines modified for use as ventilators, and

positive pressure breathing devices modified for use as ventilators.

Potential benefits of using alternatives to traditional ventilators include:

- The device may be effective in treating you if you have difficulty breathing, or other respiratory symptoms
- The device may help your condition improve and allow you to recover
- Life-supporting and potentially life-saving treatment

Potential risks of using alternatives to traditional ventilators include:

- A positive pressure breathing device cannot offer all the support a traditional mechanical ventilator can offer
- A positive pressure breathing device may expose others to aerosols that could be contagious
- Healthcare providers may not be familiar with the operation of the modified devices that are authorized

under this EUA, which could lead to use error

- Where can I go for updates and more information? The most up-to-date information on COVID-19 is available at the CDC General webpage: https://www.cdc.gov/COVID19. (https://www.cdc.gov/nCoV) In addition, please also contact your healthcare provider with any questions/concerns.

2

Table of Content: Page v

Waranty…………………………………………………………………………………………………………………………………………….III

Notices………………………………………………………………………………………………………………………………………………IV

Fact Sheet for Healthcare Providers….……………………………………………………………………………………………….V-VI

Fact Sheet for Patients…………………..………………………………………………………………………………………………….VII-VIII

Section 1 - Introduction…………………………………………………………………………………………………………………….2

Section 2 – Ventilator Overview…………………………………………………………………………………………………………6

Section 3 – Breath Types and Ventilation Mode……………………………………………………………………………….8

Section 4 –Using the Controls and Indicators……………………………………………………………………………………10

Section 5 –Controls……………………………………………………………………………………………………………………………12

Section 6 –Displays and Indicators……………………………………………………………………………………………………13

Section 7 – Monitored Data………………………………………………………………………………………………………………14

Section 8 – Ventilator Alarms……………………………………………………………………………………………………………15

Section 9 – Ventilator Checkout Tests………………………………………………………………………………………………16

Section 10 – Operating Procedure……………………………………………………………………………………………………18

Section 11 – Cleaning, Disinfecting and Sterilization……………………………………………………………………….20

Section 12 – Troubleshooting………………………………………………………………………………………………………….21

Section 1 -INTRODUCTION

This Operator’s Manual contains detailed information and instructions which when adhered to ensure the safe and effective set up, use and simple maintenance of the Bridge ventilator.

This manual is designed for use by critical care physicians, respiratory therapists or other qualified and trained personnel under the direction of a physician and in accordance with applicable state and federal laws and regulations.

Operator’s Safety Information

All operators are to read and understand the following information about Warning, Caution and Note statements before operating the Bridge ventilator.

WARNING

“WARNING” statements alert the reader to potentially hazardous situations which, if not avoided, could result in death or serious injury.

CAUTION

“CAUTION” statements alert the reader to potentially hazardous situations which, if not avoided, could result in equipment damage.

NOTE

“NOTE” statements contain additional information to assist in the proper operation of the Bridge ventilator.

Bold Text: Words that appear in bold text typically represent text as it appears on the ventilator itself, or used as emphasis.

Abbreviations: Bridge ventilator and the ventilator are used interchangeably throughout this document.

WARNING

Untrained Personnel – Only licensed and properly trained personnel should operate the ventilator. The Bridge ventilator is a restricted medical device designed for use by respiratory therapists or other properly trained and qualified personnel under the direction of a physician and in accordance with applicable state laws and regulations.

Leak Testing the Patient Breathing Circuit – The patient circuit must be leak tested before connection to the patient. In addition, the Ventilator Checkout should be used to check for correct operation of the ventilator alarms. Harm to the patient due to ineffective ventilation may result from failure to leak test the patient breathing circuit before connection to a patient. When using accessories such as heated humidifier, they must be include it in the circuit when performing leak testing.

Critical Alarms – For safety purposes, all alarms must be checked to insure proper operation.

Alarms Function Verification - All alarms must be verified as functioning properly at least daily. If any alarm malfunctions, immediately ventilate the patient with an alternative mode of ventilation and follow the troubleshooting steps.

Patient Monitoring - Patients who are dependent on a ventilator should be constantly monitored by qualified personnel. Such personnel should be prepared to address equipment malfunctions and circumstances where equipment becomes inoperative. An alternative method of ventilation should be available for all patients dependent on the ventilator, and qualified personnel should be fully familiar with emergency ventilation procedures.

Alternative Ventilation - It is recommended that an alternative means of ventilating the patient be available at all times and that all ventilator operators be fully familiar with emergency ventilation procedures.

Fire or Explosion - Operation of the Bridge ventilator in the presence of flammable gases could cause a fire or explosion. Under no circumstances is the ventilator to be operated when explosive gases are present. The presence of nitrous oxide or flammable anesthetics present a danger to the patient and operator.

Patient Breathing Circuit Disconnection - Inadvertent disconnection of the patient from the patient breathing circuit is dangerous.

Personal Injury and Electric Shock - Operation of the Bridge ventilator if any of its panels have been removed may result in electrical shock to the patient or operator.

Audible and Visual Alarms - Failure to immediately identify and correct audible and visual alarm situations may result in serious patient injury.

Equipment Malfunction or Failure - The Bridge ventilator has alarms to notify operators of certain conditions and to cease operating upon detecting possible danger. In the event of equipment failure, all ventilator operators should have an alternative method of ventilation available and be fully familiar with emergency ventilation procedures.

Improperly Functioning Ventilator - Operation of a ventilator that does not appear to be working properly may be hazardous. If the ventilator is damaged or malfunctions in any way, discontinue its use and immediately, ventilate the patient with an alternative mode of ventilation and contact Borzoo Farhang.

Ventilator Checkout Tests – Be aware that no breath is delivered to the patient during the Ventilator Checkout Test. Disconnect the patient from the ventilator and ventilate the patient using an alternative method before running the Ventilator Checkout tests.

Inspired Oxygen (FIO2) Concentration – If the patient has a variable respiratory rate, his/her minute ventilation will fluctuate. If exact concentrations of inspired oxygen (FIO2) are required to be delivered to the patient, it is recommended that an accurate oxygen analyzer with alarms be used and an air-oxygen blender utilized.

Ventilation Variables and O2 Consumption - Variations in the patient’s minute ventilation, I:E ratio and/or ventilator setting changes or equipment status (i.e. circuit leaks) affect the consumption rate of oxygen. When warranted by a patient’s condition, it is recommended that a back-up cylinder or alternative source of oxygen be available at all times.

Unauthorized Parts or Accessories – Serious harm to the patient may result from the use of unauthorized parts or accessories. Only items expressly approved by Borzoo Farhang may be used in conjunction with the Bridge ventilators.

Ultra Violet Light Sensitivity – The material used in the 3D-printed portions of the ventilator (polylactic acid) are not UV stable. Avoid exposure to direct UV light.

Patient Circuit Accessories - The use of accessories such as Heat-Moisture Exchangers or Filters create additional patient circuit resistance and in the event of a disconnection, may impede the generation of low tidal volume alarm. Perform a clinical assessment to determine if an alternative monitor (i.e. a Pulse Oximeter with an audible alarm, or a Cardio-Respiratory Monitor) should be used.

MR Safety – The Bridge ventilator is not MRI-Safe and must be avoided in MRI suits. It can cause serious damage to patients, staff and equipment in strong magnetic fields.

Cautions

Ventilator Sterilization – To avoid irreparable damage to the Bridge ventilator, do not attempt to sterilize it.

Cleaning Agents – To avoid damaging the ventilator’s plastic components, do not use cleaning agents containing ammonium chloride, other chloride compounds, more than 2% glutaraldehyde, phenols, or abrasive cleaners.

Ventilator Immersion - Do not immerse the ventilator in liquids.

Reusable Patient Circuit Components – There is no reusable patient circuit components. This ventilator is designed to work with Jackson-Rees or Mapleson D circuit. Please comply with all procedures as specified by the circuit’s manufacturer.

Front Panel Cleaning – Do not pour or spray liquid cleaners onto the front panel.

Care of Bacterial Filters – If bacterial filters are used in conjunction with the Bridge ventilator, comply with all procedures as specified by the filter manufacturer.

Wet or Damp Filters – If wet or damp filters are utilized with this device, comply with all procedures as specified by the filter manufacturer.

Oxygen Supply Contamination - The accuracy of the oxygen delivery capabilities of Bridge ventilator can be compromised by foreign debris contamination in the oxygen supply system. To reduce the risk of airborne contaminants entering the ventilator, ensure that any oxygen supply connected to the ventilator is clean, properly filtered and that the ventilator’s O2 Inlet Port Cap is securely installed on the O2 Inlet Port whenever the ventilator is not connected to an external oxygen supply.

Power Outlets – Power outlets are normally wired for a positive center contact and ground sleeve contact. Connecting the ventilator to an improperly wired outlet will cause the adapter fuse to blow and may damage the adapter or the ventilator.

Electrical Grounding – In the event of a loss of electrical protective ground, touching the ventilator could result in electrical shock. To ensure grounding and avoid this danger, use only the unmodified power cord originally supplied with the Bridge ventilator, maintained in good condition and connected to a properly wired and grounded electrical power outlet.

Do not cover the ventilator – To avoid damage to the ventilator, do not cover while operating or position relative to other objects such that the operation or performance of the ventilator may be adversely affected. Ensure that sufficient space exists around the ventilator while in use to allow free circulation of gases.

Electrostatic Discharge – The use of electrically conductive hoses and tubing is not recommended. The use of such materials may result in damage to the ventilator from electrostatic discharge.

AC Power Source - When connecting the ventilator to an AC power source, use only the approved Bridge power adapter.

Fuse Fire Hazard – Replacement of existing fuses with fuses with different voltage or electrical current ratings may cause a fire.

Ventilator Checkout Tests – The Bridge ventilator Checkout tests must be performed before initial use of the ventilator. Rerun the tests whenever a question about the ventilator’s operation arises.

SECTION 2 – Ventilator Overview

The Bridge ventilator is a lightweight, low-budget and open-source ventilator that is designed to provide the maximum functionality during the extreme shortage of medical supply during COVID-19 outbreak as a temporary measure to keep the patients alive until an FDA approved mechanical ventilator becomes available. The Bridge ventilator provides the following features:

- High performance ventilation in a small, lightweight, low-cost and single-patient-use package.
- Gear and pinion technology allows the ventilator to operate without an external compressed gas source.
- Volume controlled mode of ventilation with machine triggered breaths.
- Alarm system including high peak pressure, too high or low tidal volumes and device malfunction.
- Presets to facilitate rapid patient set-up.

Indications for Use

The Bridge ventilator is intended to provide continuous or intermittent ventilatory support for the care of the individuals who require mechanical ventilation during COVID-19 outbreak when there is no FDA approved device (ventilator) is available. The ventilator is a restricted medical device intended for use by qualified, trained personnel under the direction of a licensed physician. Specifically, the ventilator is applicable for adult patients with ideal body weight of at least 50 kg, who require positive pressure ventilation, delivered invasively (via endotracheal or tracheostomy tube). The ventilator is suitable for use in critical care settings.

CAUTION: Federal law restricts this device on the order of a physician.

Section 3 – Breath Types and Ventilation Mode

This Section contains information regarding the breath types available on the Bridge ventilator. It covers how breaths are initiated, limited and cycled, and when each breath is given.

The following terms are used in discussing how breaths are given:

Initiate: What causes a breath to be given. Breaths may be initiated by a patient trigger or by the ventilator based on the set breath rate and ventilation mode.

Limit: How the breath is controlled. Breaths may be limited to a maximum circuit pressure or flow.

Cycle: What causes the breath to be cycled from the inspiratory phase to the exhalation phase. Breaths may be cycled by the ventilator when a set time or delivered volume has been reached.

Breath Types

Breaths are defined by how they are initiated, limited and cycled. The breath types are Machine and Patient.

| Machine | Patient
Initiated By | Ventilator | Patient
Limited By | Ventilator | Ventilator
Cycled By | Ventilator | Patient

Breaths may be given in any of the following forms: Volume Control and Spontaneous. These breaths are given as described in the sections below.

In addition, the following parameters apply to all breaths:

- The Minimum Inspiratory Time is half of the expiratory time.
- The Minimum Exhalation Time is twice the inspiratory time.
- The I:E ratio is fixed at 1:2.

Volume Control Breaths

For Volume Control breaths, the set Tidal Volume is delivered over the set Inspiratory Time. The fresh gas flow to the Jackson-Rees or Mapleson D circuit must be set based on the manufacturer’s instruction for controlled ventilation. This fresh gas flow rate must be at least 3 times the patient’s minute volume if Jackson-Rees circuit is used and 70 ml/kg ideal body weight if Mapleson D circuit is used. Volume breaths may be only machine breaths.

Spontaneous Breaths

For Spontaneous breaths, please follow the manufacturer’s instruction for Jackson-Rees or Mapleson D circuit regarding fresh gas flow rates. Spontaneous breaths are patient type breaths. There is no mechanism in the Bridge ventilator to sense patient’s breaths. Perform a clinical assessment to diagnose and treat patient-ventilator desynchrony as indicated.

Ventilation Modes

The Bridge ventilator provides Mandatory Volume Control mode of ventilation.

Control mode ventilation is automatically selected when Bridge ventilator is turned on. In Control mode, Volume Controlled machine breaths are given at the rate specified by the Breath Rate setting and tidal volume at the tidal volume setting. There is no mechanism to detect patient breaths as a trigger, but spontaneous patient breaths are allowed.

Section 4 – Using the Controls and Indicators

Ventilator Controls

The following diagram shows how the Bridge front panel controls and displays are arranged.

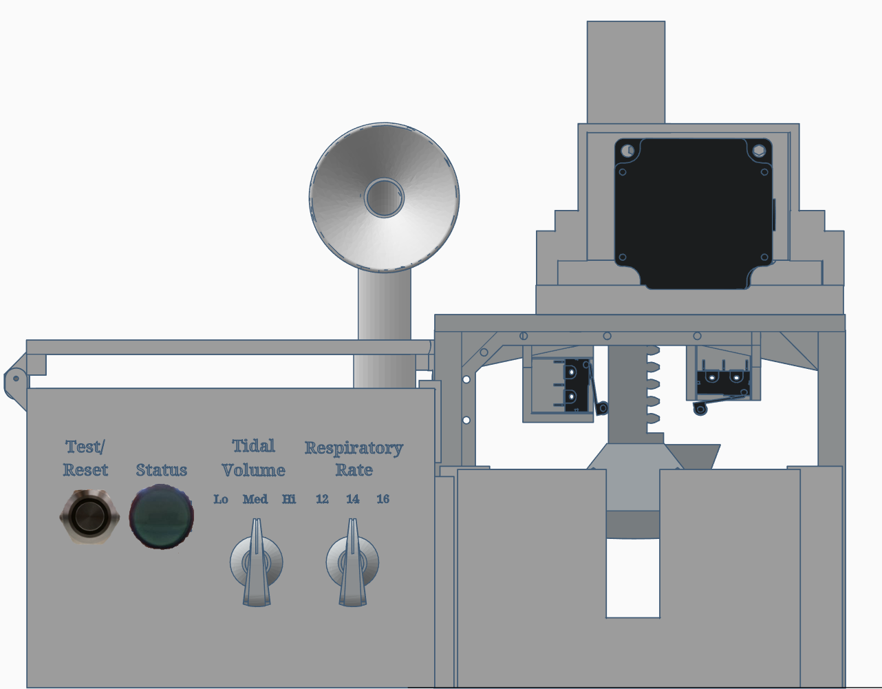
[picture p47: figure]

Setting a Control

There are 4 kinds of controls on the Bridge ventilator. They are:

- Variable Controls: Controls and alarms that have front panel displays.
- Buttons: Push buttons that perform a function.
- Set Value Knobs: Used to set control values.
- Mechanical Controls: Controls, such as Over Pressure Relief, that are hardware regulated and not operator adjustable.

The following sections describe how to set each kind of control.

Variable Controls

To set a variable control:

1. Select the control knob
2. Change the control value by rotating the Set Value knob. Rotate clockwise to increase and counter-clockwise to decrease the value.
3. An audible beep with confirm change from the previous value.

Buttons

Button control performs a function, such as ventilator checkout test or reset the tidal volume.

Push the button to activate the feature. An audible beep will confirm the push button.

Set Value Knob

Use the Set Value knob to set control values. To change the setting for a variable control, turn the knob clockwise or

counter-clockwise until the desired setting is reached. An audible beep will confirm the push button.

LED Controls

Visual alarms will be displayed as solid. A solid red LED indicates tidal volume delivery malfunction. See Ventilator Alarms section for more information. A solid green LED light indicates optimum performance. An alternating green-red LED light indicates Ventilator Checkout Test.

Control Limiting

The tidal volume setting may be affected by any of the following reasons:

- Tidal volume may vary to ensure a minimum inspiration time of matching I:E of 1:2.
- Tidal volume may vary to ensure a minimum exhalation time of matching I:E of 1:2.
- Tidal volume may vary to ensure peak pressure does not exceed limiting pressure of 40 cmH2O.
- Inadequate fresh gas flow rate to Jackson-Rees or Mapleson D circuit can result in reduced tidal volumes.

When you are updating a control, if a limited condition occurs, the red control LED will turn on solid and a continuous audible alarm will sound.

Section 5 – Controls

This section explains how each of the Bridge ventilator front panel controls work.

Breath Rate

Use the Breath Rate control (Respiratory Rate) to establish the minimum rate of machine breaths that the ventilator will deliver per minute.

To set the Breath Rate, rotate the Respiratory Rate knob clockwise or counter-clockwise. The available choices for breath rates are 12, 14 and 16 breaths per minute. Upon changing the value, an audible beep confirms the change.

Tidal Volume

Use the Tidal Volume control knob to establish the volume of gas which the ventilator will deliver during Volume Controlled breaths. Flow is delivered constantly to the Jackson-Rees or Mapleson D circuit. Inspiratory and expiratory times are set at 1:2.

Section 6 – Displays and Indicators

This section describes each of the Bridge ventilator front panel displays.

Airway Pressure

The Bridge ventilator will not show the airway pressures unless connected to an auxiliary pressure transducer and display; however, should the peak airway pressure reach 40 cmH2O, the tidal volume is reduced and the machine alarm triggered. The machine will attempt to deliver a tidal volume below the set maximum pressure of 40 cmH2O, while the continuous alarm will not shut off until an operator presses the reset button and perform the troubleshooting steps.

External Power Indicator

The External Power indicator shows the status of the external power and the ventilator is operating optimally from an external power source. When running from external power, the indicator shows solid green. If the red indicator is on, it indicates device malfunction (accompanied by a continuous audible alarm).

Section 7 – Monitored Data

This section describes each of the monitored data and how the data is calculated.

Tidal volume is derived from the stroke distance of the Bridge ventilator gear and pinion system. This was achieved empirically at the following flow rates at specific minute volumes:

Set Respiratory Rate | Set Tidal Volume | Flow Rate (L/min) | Step Distance | Actual Tidal Volume (ml)
12 | Low | 15 | 850 | 350
| Med | 15 | 1300 | 400
| High | 15 | 2000 | 450
14 | Low | 15 | 850 | 325
| Med | 15 | 1300 | 375
| High | 15 | 2000 | 425
16 | Low | 15 | 850 | 300
| Med | 15 | 1300 | 350
| High | 15 | 2000 | 400

When the Bridge ventilator is turned on, the onboard computer will record the expected location of the ventilator plate at the end expiration as well as mid-inspiration and mid-expiration. During each respiratory cycle, each mid-inspiratory and -expiratory value is compared with the expected values, and any deviation will result in activation of device malfunction alarm.

Section 8 – Ventilator Alarms

When conditions requiring immediate operator interactions are detected by the Bridge ventilator, an alarm is generated. All alarms require some action from the operator, and the audible and visual alarms will continue until the problem is corrected.

When an alarm occurs:

- An audible alarm sounds.
- The red LED light will be lit solid.

When an alarm condition clears:

- The audible alarm is silenced.
- The LED light will turn solid green.

WARNING

Critical Alarms – For safety purposes, all alarms must be checked to ensure proper operation.

Audible/Visual Alarms - Failure to immediately identify and correct audible/visual alarm situations may result in serious patient injury.

Alarms

High Pressure

When the pressure in the patient circuit is greater than 40 cmH2O, the malfunction alarm is generated. When this alarm occurs, any inspiration in progress is reduced to avoid exceeding 40 cmH2O pressure. This will result in LED light changing from green to red and an audible alarm is generated, which is sustained until reset button is pressed and troubleshooting steps taken.

Inadequate Inspiratory Tidal Volume

During each breath, if the step distance in the stepper motor during inspiration fails to activate the inspiratory switch, the malfunction alarm is generated. When this alarm occurs, the ventilator will reset the respiratory cycle and continue to deliver tidal volumes. This will result in turning changing the green LED light to red and generation of the audible alarm, which is sustained until reset button is pressed and troubleshooting steps taken.

Inadequate Expiratory Tidal Volume

During each breath, if the step distance in the stepper motor during expiration inappropriately activate the expiratory switch, the malfunction alarm is generated. When this alarm occurs, the ventilator will reset the respiratory cycle and continue to deliver tidal volumes. This will result in turning changing the green LED light to red and generation of the audible alarm, which is sustained until reset button is pressed and troubleshooting steps taken.

Section 9 – Ventilator Checkout Test

This Section details the test procedures used to verify the proper operation of the Bridge ventilator. These tests should be performed before the device is connected to the patient and as needed thereafter (at least once daily). An alternative mode of ventilation must be available during this test, and the Bridge ventilator will not provide ventilatory support during this test.

Initial Power on

Upon turning on the machine, prior to connecting to the patient, the ventilator plate will rise all the way to the top. The upper limit of the machine’s stroke distance is sensed by a sensor and saved. An audible beep occurs once this upper limit sensor is activated. Next, the down stroke is tested and upon activation of the mid-stroke sensor, a second audible beep is noted. This distance is also saved. If this initial check is free of error, the Bridge ventilator will begin delivering tidal volumes.

If any malfunction is detected in the stroke distance, the LED light will be lit solid red and a continuous audible alarm sounded. The bridge ventilator will continue to deliver a tidal volume in the presence of a malfunction but should not be connected to a patient until the malfunction is resolved.

1. Ensure that the patient is not connected to the ventilator and an alternative method of ventilation is in use.
2. Turn on the Bridge ventilator.
3. Ensure that the AC Adapter is connected to a valid AC power source and verify that the LEDs is illuminated solid green.
4. The machine will begin the test automatically.
5. The ventilator plate will first rise all the way to the top. When it is at the top, an audible single beep is generated.
6. Next, the ventilator plate is lowered halfway, and will generate another single audible beep.
7. If no malfunction is detected, the ventilator plate will start delivering tidal volumes.
8. On the other hand, failure to pass this initial power on test would result in a continuous alarm and turning on the red LED solid.
9. Single-pressing the reset button will result in momentary turning the alarm off restarting the respiratory cycle based on the previously recorded stroke distances.
10. Double-pressing the reset button will restart the Ventilator Checkout Test resultant on resetting the stroke distances and recording those values for the following respiratory cycles.
11. Follow the troubleshooting steps.

Alarm Test

1. Disconnect the patient from the ventilator and ventilate the patient using an alternative method.
2. Ensure that the AC Adapter is connected to a valid AC power source and verify that the External Power Status LEDs is illuminated.
3. Turn the Respiratory Rate knob to 12 and Tidal Volume to low.
4. Turn the Respiratory Rate knob clockwise to 14 and then to 16. Turn the Tidal Volume knob to med and then to high. With each change, an audible alarm (single beep) must be heard.

Control Test

1. Disconnect the patient from the ventilator and ventilate the patient using an alternative method.
2. Ensure that the AC Adapter is connected to a valid AC power source and verify that the External Power Status LEDs is illuminated.
3. Turn the Respiratory Rate knob to 12 and Tidal Volume knob to low.
4. As the bridge continues to push on the inflatable bag of the Jackson-Rees or Mapleson D circuit, count the breaths in 10 seconds and multiply by 6. This should correspond to 12 breaths per minute. Repeat the procedure at Respiratory Rate set at 14 and 16.
5. As the Tidal Volume knob is set to low, note the stroke distance of the Bridge ventilator. As you increase the Tidal Volume to med and high, you should see a larger stroke distance in the machine.

Leak Test

1. Disconnect the patient from the ventilator and ventilate the patient using an alternative method.
2. Follow the Jackson-Rees or Mapleson D manufacturer’s recommendation regarding leak test.

Malfunction Alarm

1. Disconnect the patient from the ventilator and ventilate the patient using an alternative method.
2. Ensure that the AC Adapter is connected to a valid AC power source and verify that the LEDs is illuminated solid green.
3. Activate the top vertical limit switch by hand (by pressing on the switch in the underside of the motor).
4. This should lead to a continuous audible alarm since the machine senses a different stroke distance (delivered tidal volume) than the expected stroke distance (delivered tidal volume).
5. Press the reset button to turn off the alarm.
6. Activate the top horizontal limit switch by hand by pressing on the switch in the underside of the motor.
7. This should lead to a continuous audible alarm.
8. Press the reset button to turn off the alarm.

Section 10 – Operating Procedures

This section describes how to turn the Bridge ventilator on and off, and how to set up the ventilation modes.

To Turn the Ventilator On

1. Connect the unit to an external source of power.
2. Set the on/off switch to on
  - The External Power LED is lit green to indicate the external power source connection and absence of any errors.
  - The bridge ventilator’s stepper motor will begin moving the ventilator plate all the way to the top (Figure 2) and begin tidal volume breaths.
  - If there are any errors found, the LED light will be lit solid red and a continuous audible alarm sound.
  - In the absence of any errors, the green LED light will continue to be lit solid and no alarms will be sounded
  - Pressing the reset button will turn off the alarms and reinitiates the respiratory cycle.

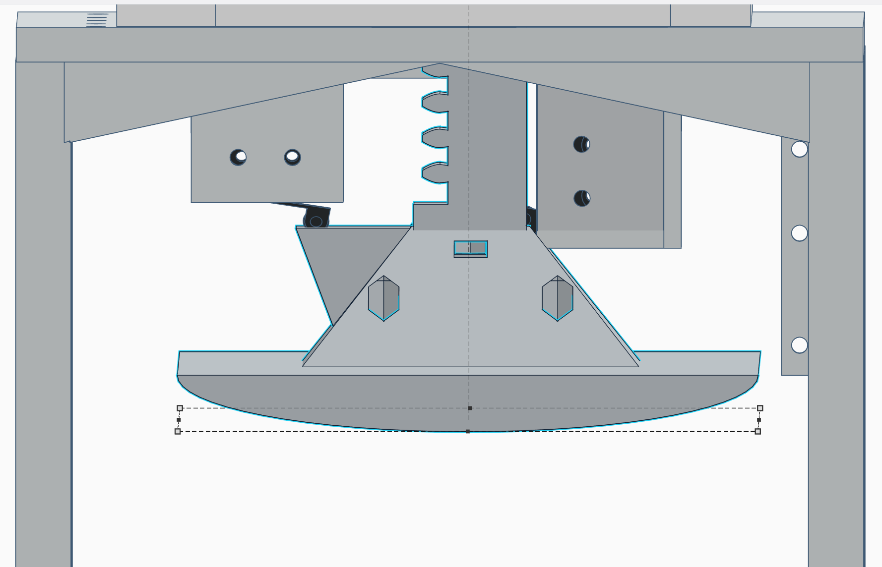
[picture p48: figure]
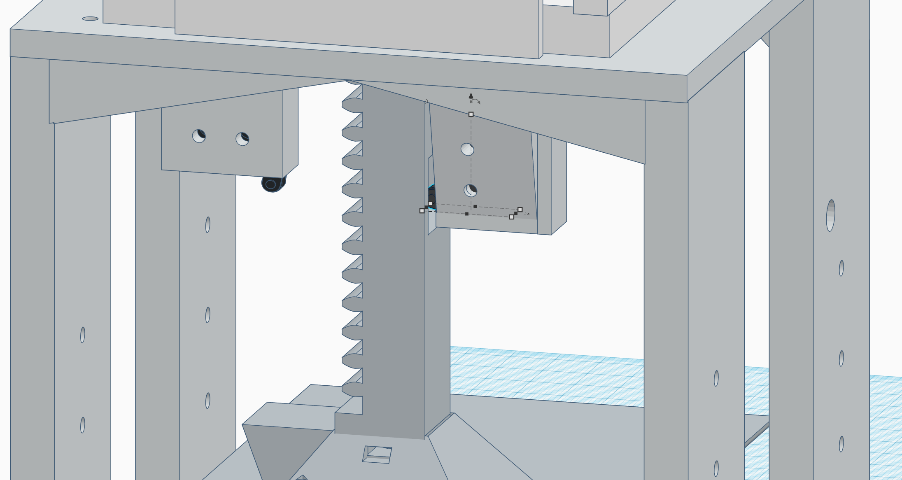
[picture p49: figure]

FIGURE 2. Upper Limit and Mid-Stroke Switches

3. Ensure adequate oxygen supply is available for Jackson-Rees or Mapleson D circuit.
4. Perform a leak test of the patient Jackson-Rees or Mapleson D circuit (as per manufacturer’s instruction) prior to connecting the ventilator to the patient.
5. Connect the patient circuit to the ventilator.
6. If the Power On Self Tests fail, the red LED light will be lit solid and a continuous alarm sounded.
  - Silence the alarm by pushing the Silence Reset button.
  - Discontinue use of the ventilator and ventilate the patient with an alternative mode.
  - Follow the troubleshooting steps.
  - If the problem is not resolved, refrain from connecting this device to the patient.

Before connecting the ventilator to a patient, follow the checkout procedures.

To Turn the Ventilator Off

1. Disconnect the ventilator from the patient.
2. Switch the power switch to off. The ventilator ceases operation, the green LED light will turn off.

Reset Button

Single-press of the reset button will turn off the continuous malfunction alarm temporarily and will restart the tidal volume breaths based on the previously recorded stroke distances (at the prior Machine Test). If a malfunction is detected, the continuous alarm will be generated and the patient must be ventilated with an alternative method.

Double-press of the reset button will turn off the continuous alarm temporarily and will restart the machine test. This will result in a new recording of expected stroke distances and initiation of tidal volume breaths. During the test, the LED light will alternate between red and green. If the machine continues to detect a malfunction, the LED light will be lit solid red and a continuous alarm generated.

Section 11 – Cleaning, Disinfecting and Sterilization

Cleaning the Ventilator

All ventilator external surfaces should be cleaned prior to initial use. To clean the ventilator:

- Wipe the exterior surfaces of the ventilator with a clean, damp cloth. The use of an anti-bacterial cleaning solution is recommended. Be sure to wipe away any residual cleaner.
- Ensure no liquid enters the electronics box.

CAUTION

Ventilator Sterilization – To avoid irreparable damage to the Bridge ventilator, do not attempt to sterilize the Bridge ventilator.

Cleaning Agents – To avoid damaging the ventilator’s plastic components and front panel, do not use cleaning agents containing ammonium chloride, other chloride compounds, more than 2% glutaraldehyde, phenols, or abrasive cleaners.

Ventilator Immersion - Do not immerse the ventilator in liquids.

The Bridge ventilator is considered single-patient use. Do not attempt to use the same device on multiple patients. Follow the manufacturer’s instruction on the use of Jackson-Rees or Mapleson D circuit (also single-patient use).

Section 12 - Troubleshooting

Ensure that the patient is not connected to the Bridge ventilator during the troubleshooting steps and an alternative method of ventilation is utilized, as the machine will not deliver tidal volumes during the test.

A single beep denotes normal function when a parameter is set or a parameter is changed. For example, during the initial power on test, a single beep is generated to denotes recording the top of the stroke distance (expected location of the ventilator plate at the end of expiration) and the second single beep denotes the location of mid-stroke (expected location of the plate during inspiration and expiration of a specific set tidal volume. Additionally, when the control knobs are rotated to change the respiratory rate or tidal volume, a single beep denotes confirmation of a change in that parameter.

There is no silence button incorporated into the Bridge ventilator. The reset button will momentarily turn off the continuous alarm and initiates resets the respiratory cycle. If the machine continues to malfunction, the continuous alarm will be generated again and the machine should not be connected to the patient.

1. The Bridge ventilator malfunction
  a. Initial Power on Test Failure
    i. Ensure there is no object obstructing the stroke path.
    ii. Remove any object around the balloon of the Jackson-Rees or Mapleson D circuit.
    iii. Ensure the balloon of the circuit in the center of the ventilation chamber of the Bridge.
    iv. Perform the leak test of the circuit.
    v. Check integrity of the sensors located under the motor bridge.

Once the above steps are taken, double-press the reset button to restart the Initial Power on test. If no continuous alarm is sounded, the machine has passed the test and ventilation is resumed.

  b. Alarm Failure
    i. If the alarm test does not result in a continuous audible alarm, disconnect the machine from the patient and utilize an alternative mode of ventilatory support.
  c. Control Failure
    i. If the respiratory rate and/or tidal volume knobs fail to change the respiratory rate and tidal volume respectively, disconnect the machine from the patient and utilize an alternative mode of ventilatory support.
  d. Malfunction Alarm
    i. If the Bridge ventilator sounds a continuous alarm, follow the procedures for the Initial Power on Test Failure.
  e. Other Malfunctions
    i. For all other malfunctions, disconnect the machine from the patient and utilize an alternative mode of ventilatory support.
2. Circuit Malfunction
  a. Please follow the instructions provided by the circuit manufacturer for troubleshooting tips.

Report Adverse events, including problems with test performance or results, to MedWatch by submitting the online FDA Form 3500 (https://www.accessdata.fda.gov/scripts/medwatch/index.cfm?action=reporting.home) or by calling 1-800-FDA-1088

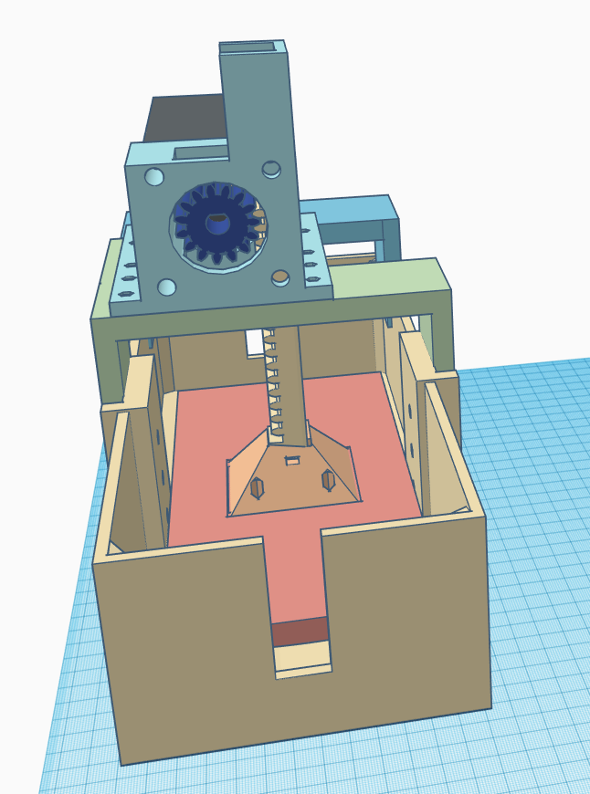
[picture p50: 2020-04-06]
3D Print Files/Vent Front.PNG

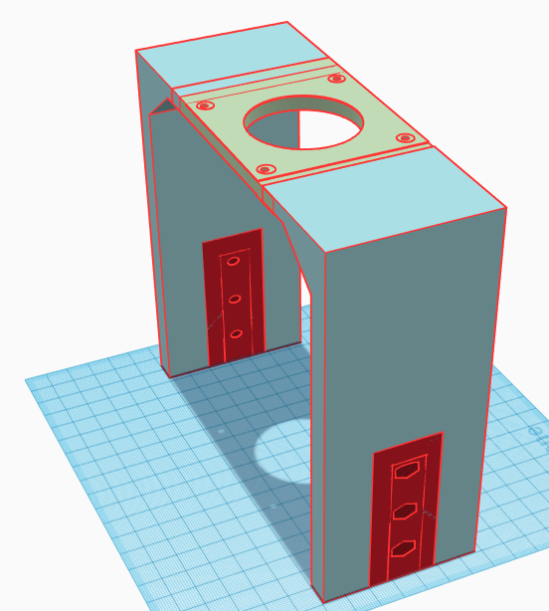
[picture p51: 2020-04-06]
3D Print Files/VentCUBase.PNG

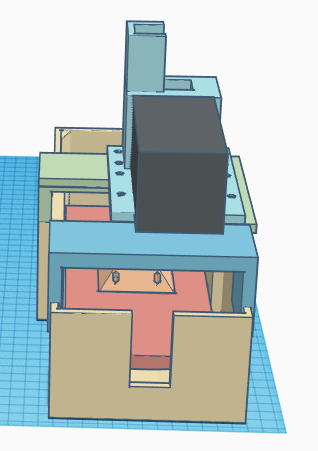
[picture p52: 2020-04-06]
3D Print Files/VentBack.PNG

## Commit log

2020-03-29 Create Arduino Sketch
2020-04-06 Update Arduino Sketch

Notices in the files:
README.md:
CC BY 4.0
